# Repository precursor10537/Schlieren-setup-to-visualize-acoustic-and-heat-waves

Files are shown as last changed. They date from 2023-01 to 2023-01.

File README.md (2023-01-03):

# Schlieren setup to visualize acoustic and heat waves
Developing a working Schlieren imaging setup to visualize heat waves and modifying it to visualize acoustic waves. 
## Basic Principles
Small-scale perturbations in the density of air due to gases and pressure waves cause minor alterations in the refractive
index as well. These slight changes in the refractive index cause phase speed differences in light, obscured to the eye. Change in phase speed as light passes through a
medium is termed as refraction. Schlieren visualization translates this refraction of light through a medium into changes in intensity that can be perceived
as regions of light and dark.

A light ray passing orthogonally through a change in refractive index will experience a change in phase velocity
but will continue traveling in the same direction undeflected [1]. If the light ray intersects the change in refractive index obliquely, it will bend towards
the region with greater “n” dictated by Snell’s law:



For a light ray travelling in the z-direction intersecting a region of gradient variation in refractive index, the ray curvature and its refraction is given by:



These angular ray deflections caused due to refraction are made perceivable by the Schlieren visualization setups [1].

## Z-Type 2-Mirror Schlieren system
The Z - Type 2-Mirror Schlieren System utilizes two oppositely tilted, on-axis parabolic mirrors as shown in Figure 3. The combination of a diverging light beams from a slit source, 
an opposite converging beam, and the collimated light between the two mirrors through the test area suggests the letter “z” [3].


 
Schematic of Z-Type 2-Mirror Schlieren System [1]

Despite the slight tilt, the mirrors are symmetrical on-axis parabolas. A minimum distance between the field mirrors of about 2f (where f is the mirror focal length) is maintained to provide space for the test area. 
This gives an inherent advantage of a larger field-of-view to the Z-type setup [3]. Furthermore, the Z-type setup occupies little area for assembly and operation which saves space in the lab. 
For a given budget, z-type setup is much more cost efficient than the lens type schlieren setup delivering a comparable performance [1]. 

## Theoretical Modeling

Computational fluid dynamics (CFD) methods are employed on supercomputers to solve equations of motion for inviscid and viscous flows by numerical calculations. 
These CFD calculations compute the output Schlieren images that are later validated by experimental results [6]. 
However, the intention of the project objectives was to gauge the upper limit bound of the sensitivity the given setup could achieve. 
Hence, CFD calculations are not required to calculate the spatial differential illuminance (relative dark and bright regions on the Schlieren Image). 
The simplistic model developed in Python takes the dimensions/specifications of the components used as input parameters to estimate sensitivity of the setup.

The model first computes the magnitude of strain caused by pressure waves corresponding to a range of frequencies using the following equation:



The variations in the refractive index are computed to obtain the perturbed refractive index as follows:



For "i" number of light rays with arbitrary (miniscule) incidence angles the model computes the refraction angles and the vertical displacement suffered by the light rays due to the
fluctuating refractive indices. 
The model considers a 2D force-field of pressure waves dependent on ultrasound device dimensions to perform the computations.
Differential illuminance intensity was calculated based on the knife-edge cutoff value and the dimensions of the focal point projected by the utilized parabolic mirrors.
The computed differential illuminance was plotted as a function of changes in pressure. 
The sensitivity of the setup is obtained as the slope dI/dP of the output graph as shown in Modeling Results.

## Modeling Results
An estimate of sensitivity was calculated for the following range of inputs tuned to our developed setup:



Modeling output to calculate the sensitivity of the setup

Results indicate that for every 5 kPa increase in pressure, we see 45.03 lumen/m2 dark (bright) levels due to the obstruction of refracted light rays by knife edge.

## Experimental Setup




## Hardware

* Light source - 
The LED light source, MCWHLP1 Mounted LED, used has an output of 41.3 W/m2 (~2828 lumen/m2) lumens. 
An LED cover was needed to constrict the light source to a single point 1mm. 
Such a cover was designed, and 3D printed [4] to fit over the LED Light source.



Front and side views of the LED light source and the LED driver



3D rendering of the designed LED cover and images of 3D printed parts

To perform the heat wave visualization, the LED light source is placed on a constant maximum intensity for imaging. 
To perform the ultrasonic wave visualization, the LED was placed on a modulated driver; tuning the LED to strobe to a corresponding duty cycle of a pulse wave similar to that of the pressure wave frequency will allow for increased contrast levels in experimentation.

* Screen Projection and Knife Edge - 
A paper screen mounted on stand for rigidity and stability was used to project the schlieren imaging, allowing for easy maneuvering to capture the reflection. 
A standard knife edge was mounted onto a stand for rigidity and stability to allow for easy maneuvering to locate the focal point.



Screen used to project the image



Position and mount of the knife edge used

* Parabolic Mirrors -
Optics selection within a Schlieren setup are one of the more prominent drivers of the result resolution and sensitivity. 
As optics increase in size, there is an increase in usable the field of view. 
However, the largest limitation is price; larger aperture optics are more expensive than similar smaller ones [4][2].
The parabolic mirrors have a diameter of 60cm, with a focal length of 37.5 cm. 
Note, a compromise for the larger diameter is the likelihood of spherical aberrations, a result that can impact the imaging.

Parabolic mirror mounts were designed, and laser cut with 6mm Acrylic sheets. 



Designed layout of parabolic mirror holder to be laser cut



Assembled and laser cut holder with parabolic mirror placed

* Acoustic Wave Source - UltraHaptics system -
UltraHaptics Touch is the system used to source the acoustic waves. 
This system focuses ultrasound projections into discrete points to provide a multi-point haptic feedback as a users’ hands are hovered over an interactive surface [5], to provide haptic feedback. 



UltraHaptics Touch System

## Experimental Results
Experimentation of the Schlieren setup was broken down into two parts (1) to detect heat waves and (2) to detect sound waves. 
The benefit of visualizing heat waves was to validate the experimental setup and fine tune the resolution and sensitivity of the setup prior to testing acoustic waves.

* Imaging Heat Waves - 
The setup to visualize heat wave was successful. 
A soldering iron was used as a heat source, set at 400C and the resulting image can visualize the differences as heat waves propagate from the source.



* Imaging Acoustic Waves -
The setup to visualize acoustic waves was unsuccessful.  

## Discussions
The working principles of a Schlieren system applied to visualize heat waves was simple, requiring adjustments to the angles and focal lengths to identify the optimal locations for the knife edge, screen, and LED light source. 
The operational parameters were all adjusted to obtain as sharp of a contrast with a larger field of view and as little distortions as possible. 
One of the limitations with the current parabolic mirror was the presence of surface aberrations. 
Such imperfections can be visualized in the resulting image, where there are a series of artifacts across the whole field of view. 
This reflects off the surface imperfections visible as shown.



Surface of parabolic mirror with surface imperfections circled in red
 
Further observations note that in addition to the parabolic mirror, there were limitations to the LED light source that resulted in lower contrast,
sensitivity, and resolution. 
The LED light required an LED cover to constrict the light source, a part that was designed and 3D printed with a diameter of 1mm. 
Two main factors were the 3D printing material and the diameter. 
The material used was not truly opaque, allowing light leakage to the surrounding. 
Furthermore, the diameter should be made even smaller, allowing for a single light source to be focused even further upon refractions.
This was noticed as the refractions past the second concave mirror did not result in a single focal point, rather an ellipse. 
It is noted that this is also attributed to the mirror surface aberrations. 

Although visualization of heat waves was successful, the resulting image did lack the resolution and contrast to visualize smaller changes of heat waves, i.e., body heat from a users’ hand
or breath. 
Because of this, the inability to generate a higher contrast image with the system results with difficulty when translating to acoustic waves. As the
LED light source was placed in a strobing function at a frequency of 40kHz, it aimed to increase the contrast of the UltraHaptics ultrasonic wave output.
However, this was not enough to account for the aforementioned equipment limitations of the LED light sources and the parabolic mirrors.

The theoretical model generated sought to detail the sensitivity output to expect given the current experimental setup input
factors; it suggested a realizable sensitivity of 45 lumen/m2 5kPa. 
Theoretically, the given experimental inputs should provide a working image, however, the equipment limitations did not allow for such sensitivity values to be feasible.

## References
[1] Settles, G. S. (2012). Schlieren and Shadowgraph Techniques: Visualizing Phenomena in Transparent Media (Experimental Fluid Mechanics) (Corrected ed.). Springer.

[2] Lim, T. T., & Smits, A. J. (2012). FLOW VISUALIZATION: TECHNIQUES AND EXAMPLES (2ND EDITION) (2nd ed.). IMPERIAL COLLEGE PRESS.

[3] Vasiliev, L. A. Schlieren methods. ed. A. Baruch. Israel Program for Scientific Translations,New York, 1971

[4] Miller, V. A., & Loebner, K. T. (2016, September 13). Smartphone Schllieren. Arxiv.Org. Retrieved May 18, 2022, from https://arxiv.org/pdf/1609.04298.pdf

[5] Carter, T., Seah, S., Long, B., & Drinkwater, B. (2013). UltraHaptics: multi-point mid-air haptic feedback for touch surfaces. UIST ’13: Proceedings of the 26th Annual ACM Symposium on User Interface Software and Technology, 505–514. https://doi.org/10.1145/2501988

[6] Philbert, M., J. Surget, and C. Veret. Shadowgraph and schlieren . Chap. 12 of Handbook of Flow Visualization. . Hemisphe re Pub., Washington, ed. I, pp. 189-217, 1989.

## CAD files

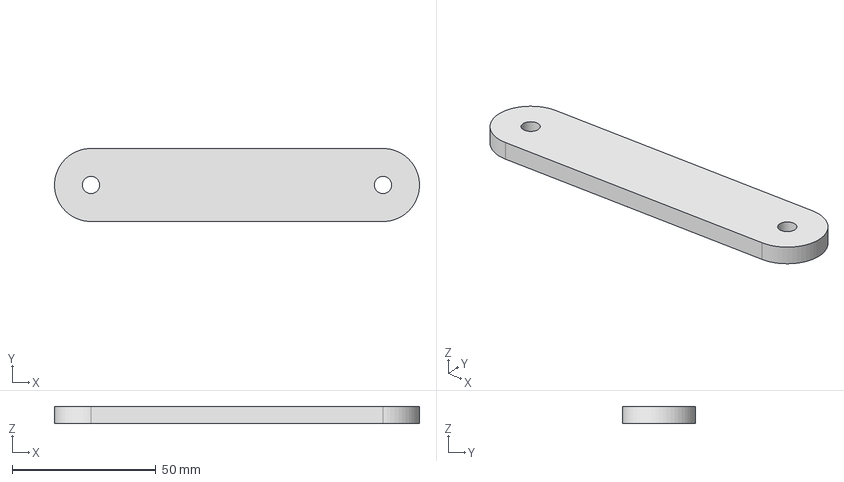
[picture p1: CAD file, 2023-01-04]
Holder_Part5_qty3.igs
127.0 x 25.4 x 6.00 mm

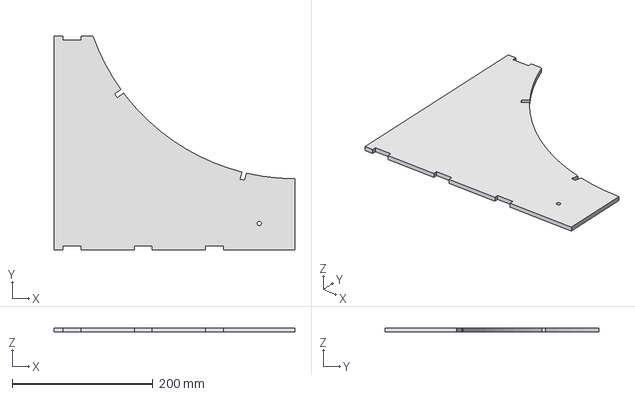
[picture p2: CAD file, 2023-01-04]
Holder_part1_qty2.igs
342.9 x 304.8 x 6.00 mm

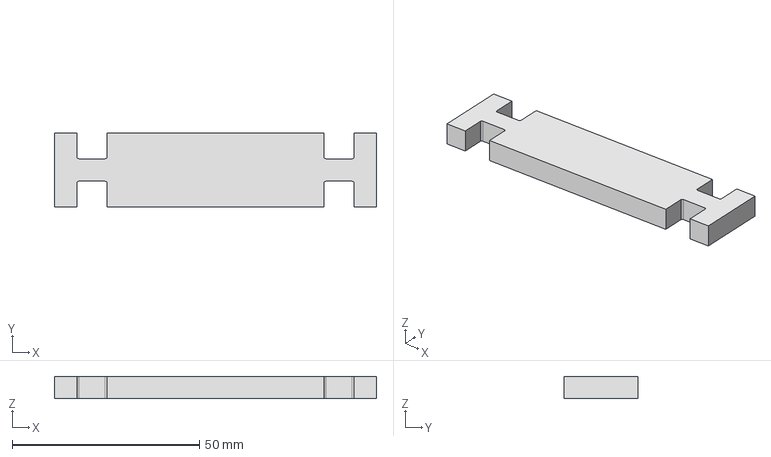
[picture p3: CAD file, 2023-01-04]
Holder_Part7_qty6.igs
85.9 x 19.6 x 6.00 mm

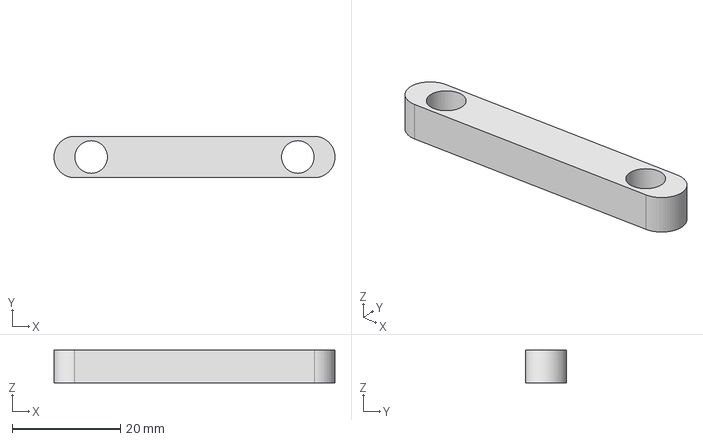
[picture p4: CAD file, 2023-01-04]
Holder_Part6_qty3.igs
51.8 x 7.62 x 6.00 mm

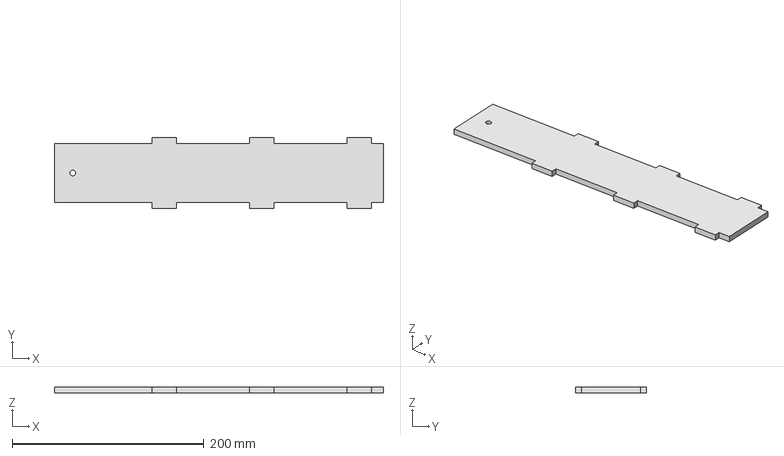
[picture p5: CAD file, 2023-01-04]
Holder_part4_qty2.igs
342.9 x 73.7 x 6.00 mm

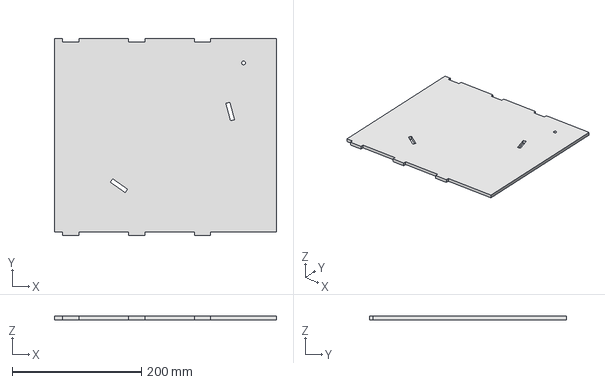
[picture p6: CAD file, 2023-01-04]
Holder_part3_qty2.igs
342.9 x 304.8 x 6.00 mm

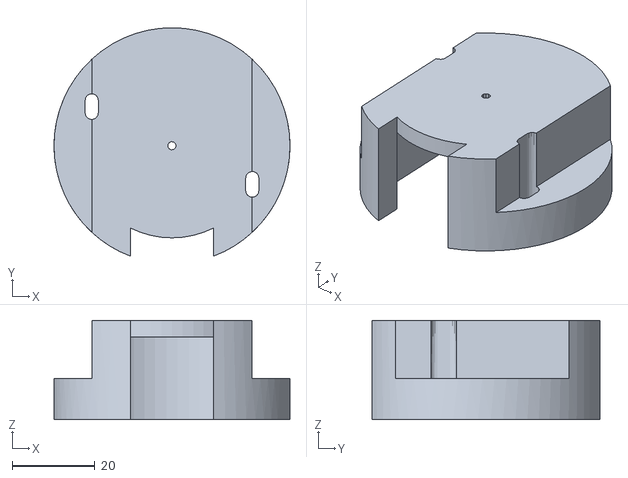
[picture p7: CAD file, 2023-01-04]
LED Cover.stl
57.0 x 55.2 x 24.0

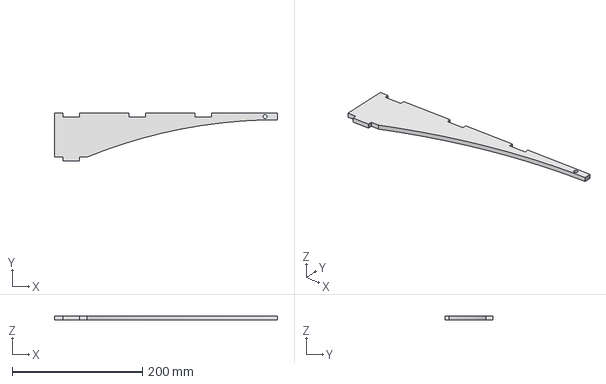
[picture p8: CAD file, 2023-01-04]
Holder_part2_qty2.igs
342.9 x 73.7 x 6.00 mm
